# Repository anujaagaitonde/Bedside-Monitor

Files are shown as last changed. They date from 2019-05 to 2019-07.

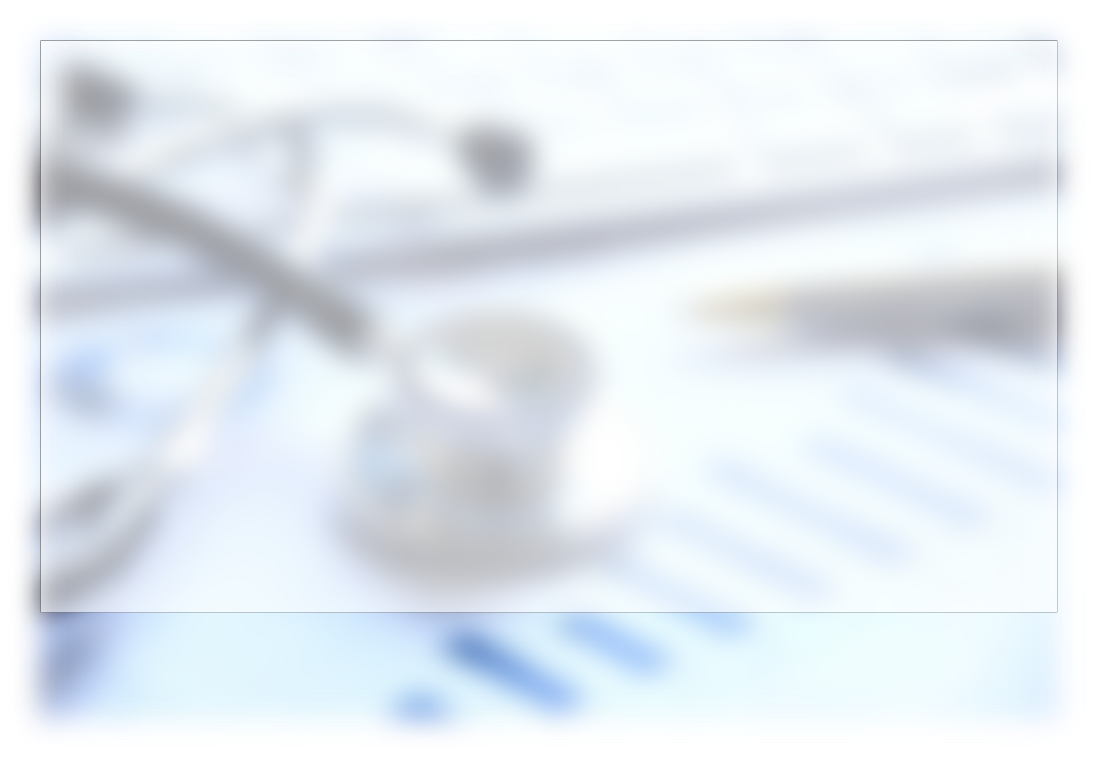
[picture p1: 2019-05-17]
Web/images/bg_image@2x.png

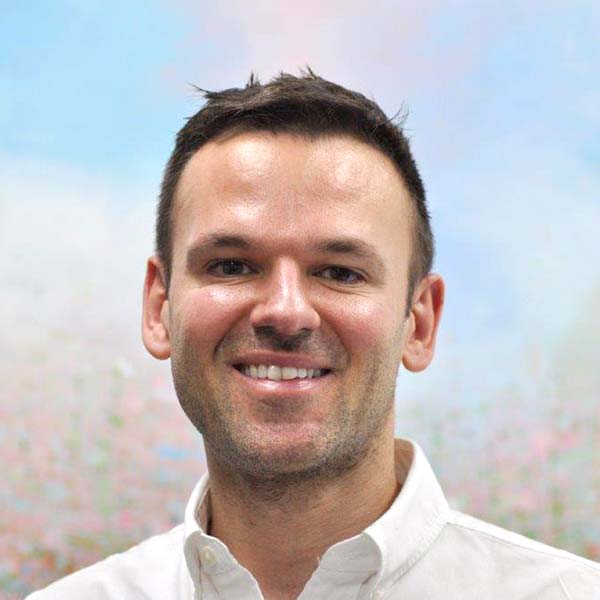
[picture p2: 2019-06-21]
Web/images/dr_profile_pic.jpg

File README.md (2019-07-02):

# LifeLine

LifeLine is a low-cost Internet-of-Things vital sign monitor with real-time illness prediction which allows doctors to monitor several patients at once from a remote location. Custom circuitry interfaces sensors to measure the patient's vital signs with any Raspberry Pi. Sensor data is displayed live on a bedside monitor and is live-streamed to a cloud-based database. A webapp allows doctors to monitor all their patients live, as well as viewing patient history over the past 24 hours. Sensor data is processed in real-time by a machine learning algorithm to detect and predict a critical event in the patient's status, which is relayed to the doctor via an instant notification in the webapp.

## Documentation

For further information about this project, visit our [wiki](https://github.com/anujaagaitonde/Bedside-Monitor/wiki):
* [1. Home](https://github.com/anujaagaitonde/Bedside-Monitor/wiki/1.-Home)
* [2. Product Design History](https://github.com/anujaagaitonde/Bedside-Monitor/wiki/2.-Product-Design-History)
* [2.1 Hardware and Firmware](https://github.com/anujaagaitonde/Bedside-Monitor/wiki/2.1-Hardware-and-Firmware)
* [2.2 Web App](https://github.com/anujaagaitonde/Bedside-Monitor/wiki/2.2-Web-App)
* [2.4 Deep Learning Model](https://github.com/anujaagaitonde/Bedside-Monitor/wiki/2.3-Deep-Learning-Model)
* [3. Meeting Records](https://github.com/anujaagaitonde/Bedside-Monitor/wiki/3.-Meeting-Records)
* [4. Innovation](https://github.com/anujaagaitonde/Bedside-Monitor/wiki/4.-Innovation)
* [5. Report of Ethical Consequences and Sustainability](https://github.com/anujaagaitonde/Bedside-Monitor/wiki/5.-Report-of-Ethical-Consequences-and-Sustainability)
* [6. Testing](https://github.com/anujaagaitonde/Bedside-Monitor/wiki/6.-Testing)
* [7. Getting Started](https://github.com/anujaagaitonde/Bedside-Monitor/wiki/7.-Getting-Started)

## About this Repository

* **[3D Printed Case:](https://github.com/anujaagaitonde/Bedside-Monitor/tree/master/3D%20Printed%20Case)** Contains 3D print and laser cut files for casing.
* **[GUI Mockups:](https://github.com/anujaagaitonde/Bedside-Monitor/tree/master/GUI%20Mockups)** Contains mockups for bedside LCD GUI.
* **[Hardware:](https://github.com/anujaagaitonde/Bedside-Monitor/tree/master/Hardware)** Contains PCB design files for PPG sensor and custom Raspberry Pi Hat.
* **[Machine Learning:](https://github.com/anujaagaitonde/Bedside-Monitor/tree/master/Machine%20Learning)** Contains illness prediction scripts.
* **[Pi:](https://github.com/anujaagaitonde/Bedside-Monitor/tree/master/Pi)** Contains the files to be run on the device Raspberry Pi and its associated libraries.
* **[Print:](https://github.com/anujaagaitonde/Bedside-Monitor/tree/master/Print)** Contains poster, leaflet and slideshow files used during demonstration.
* **[Web:](https://github.com/anujaagaitonde/Bedside-Monitor/tree/master/Web)** Contains webapp mockups and source files.

## The Project Team

* **Gasim Ahmed:** *Firmware and Machine Learning Developer*
* **Yasmin Baba:** *Hardware Designer*
* **Anuja Gaitonde:** *Web / GUI Developer and Print Promotion Designer*
* **Dayan Graham:** *Web / Cloud Developer and Casing Designer*
* **Prithvi Menon:** *Machine Learning Developer*
* **Omar Muttawa:** *Firmware Developer*

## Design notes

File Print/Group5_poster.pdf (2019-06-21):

# lifeline: THE LOW COST, IoT VITAL SIGNS MONITOR WITH REAL-TIME ILLNESS PREDICTION

## gasim ahmed, yasmin baba, anuja gaitonde, dayan graham, prithvi menon, omar muttawa academic supervisor: tim constandinou, client: miguel hernandez, mf technologies

THE PROBLEM | THE SOLUTION

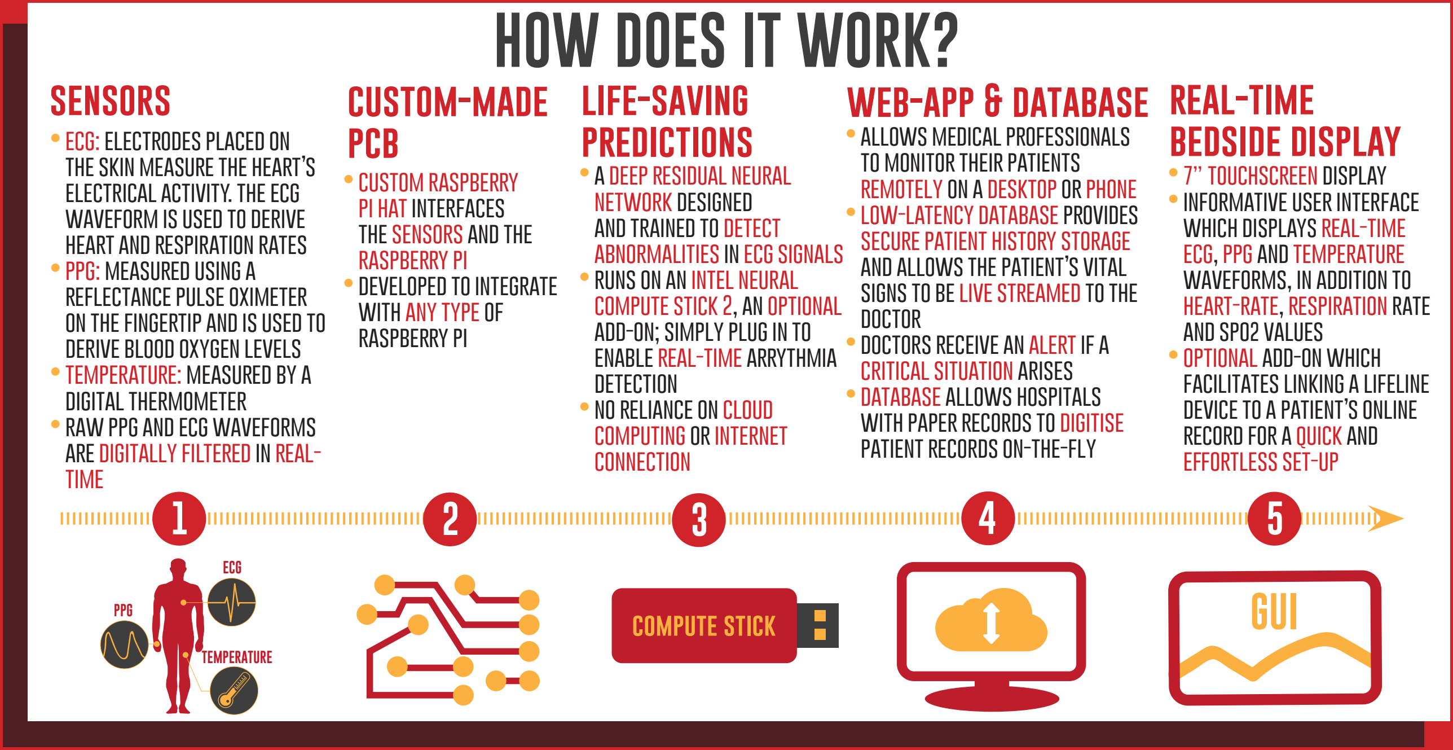
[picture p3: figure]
HOW DOES IT WORK?; sensors; custom-made; pcb; life-saving predictions; web-app & database real-time bedside display; • ecg: electrodes placed on the skin measure the heart’s electrical activity. the ecg waveform is used to derive heart and respiration rates • ppg: measured using a reflectance pulse oximeter on the fingertip and is used to derive blood oxygen levels • temperature: measured by a digital thermometer • raw ppg and ecg waveforms are digitally filtered in real- time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

# future work

## lifeline

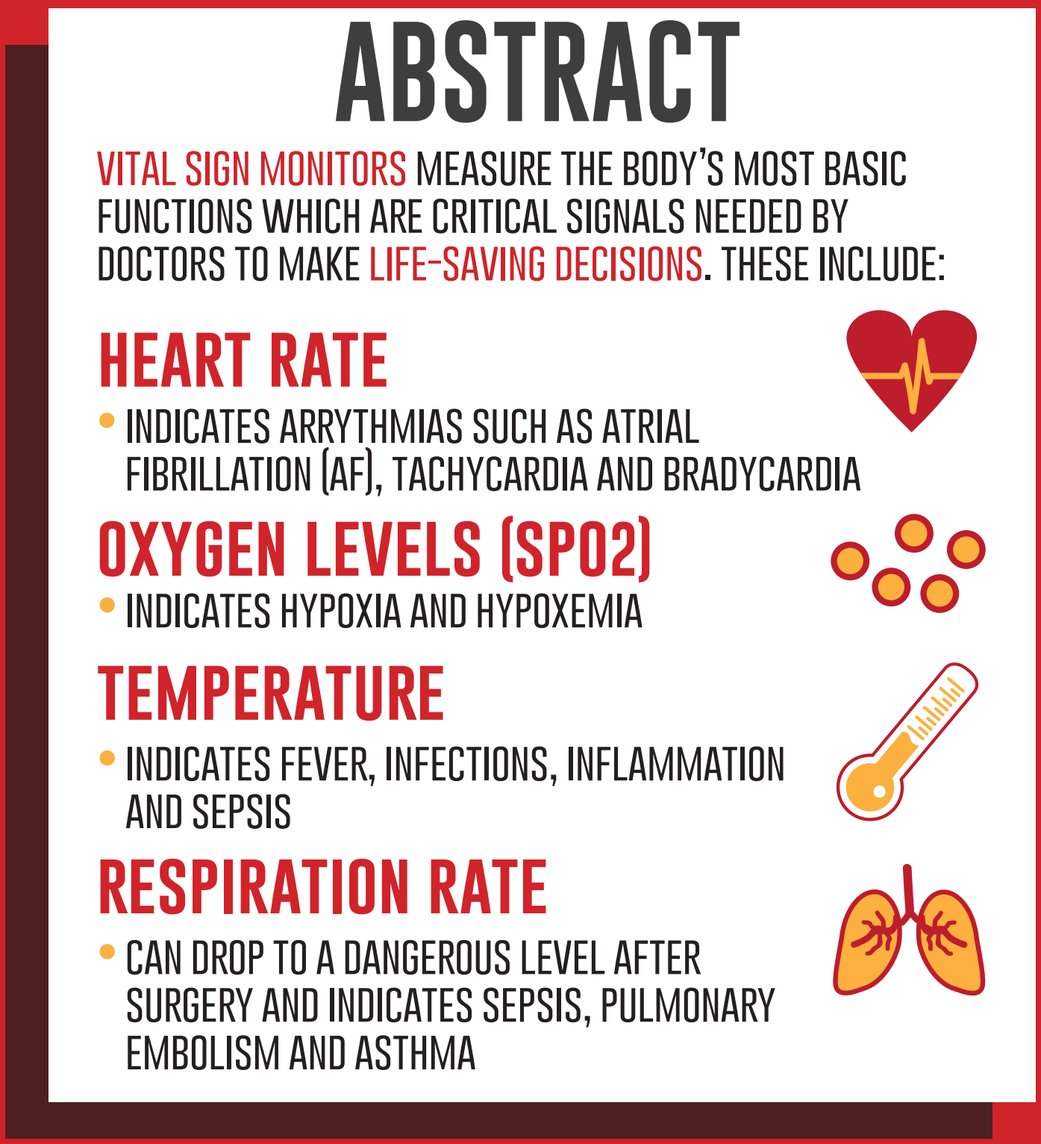
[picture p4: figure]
ABSTRACT; heart rate; oxygen levels (spo2); temperature; respiration rate; fibrillation (af), tachycardia and bradycardia; • indicates hypoxia and hypoxemia; • indicates fever, infections, inflammation and sepsis; • can drop to a dangerous level after surgery and indicates sepsis, pulmonary embolism and asthma

vital sign monitors measure the body’s most basic
functions which are critical signals needed by
doctors to make life-saving decisions. these include:

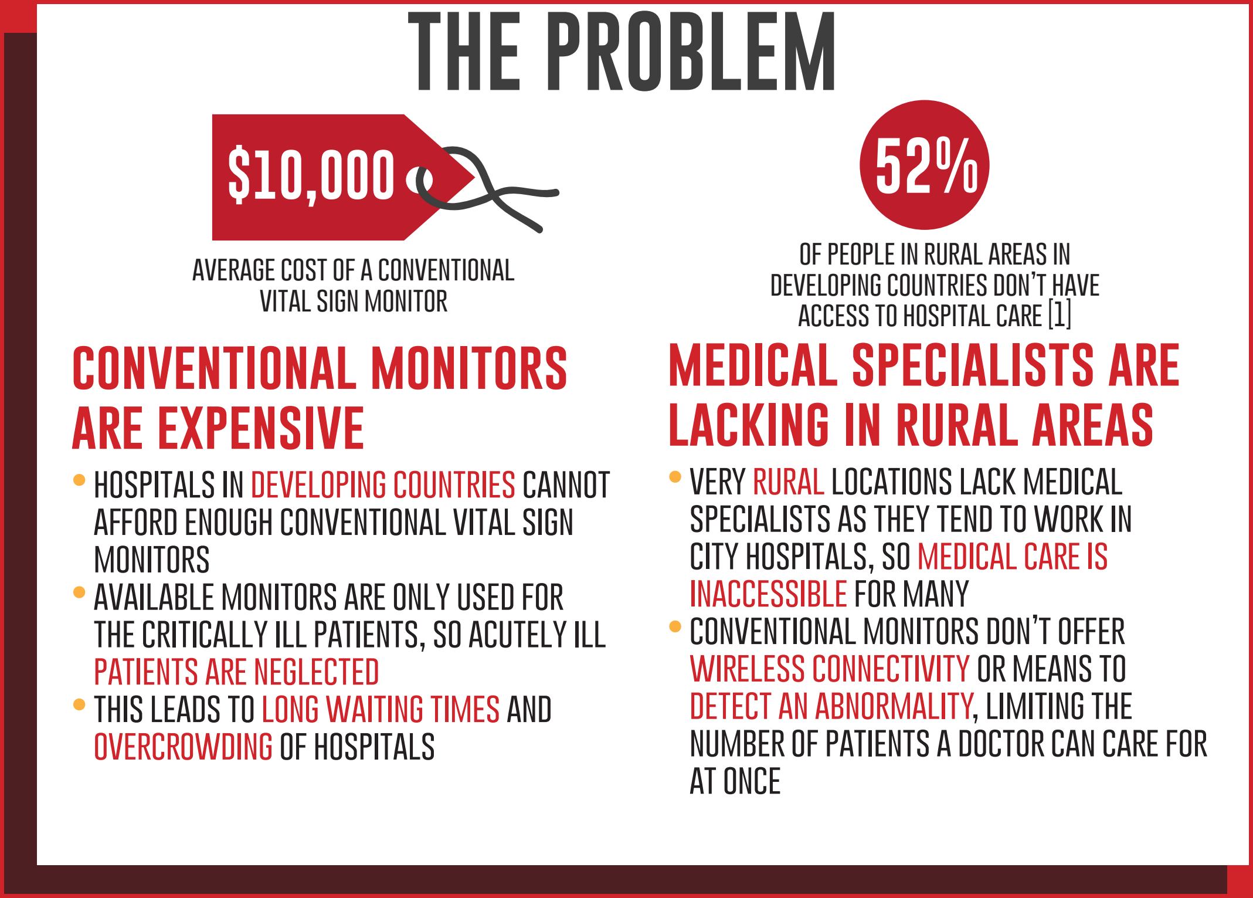
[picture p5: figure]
conventional monitors are expensive; medical specialists are lacking in rural areas; average cost of a conventional vital sign monitor; of people in rural areas in developing countries don’t have; afford enough conventional vital sign monitors • available monitors are only used for; patients are neglected • this leads to long waiting times and overcrowding of hospitals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

access to hospital care [1] • indicates arrythmias such as atrial

- hospitals in developing countries cannot

the critically ill patients, so acutely ill

- low-cost iot device that can remotely measure a patient’s vital signs from any location
- live patient data is streamed to a doctor’s desktop or phone, whilst built-in machine learning algorithms detect any abnormalities
- allows doctors to care for several patients in several locations at once, whilst alleviating the over-demand for hospital beds
- features a modular design which allows units to be customised specific to patient needs. this means hospitals can cut costs by only having to buy and / or replace the parts they actually need.
- depending on the chosen customisation option, lifeline costs between £44 -£166.
- lifeline is a durable product, housed in a secure and biodegradable 3d printed pla case

in the future, lifeline would be improved as follows:
- integrate non-invasive blood pressure monitoring
- introduce online learning to improve the abnormality detection algorithm
- research optimal digital filter methods for ecg and ppg real-time processing
- increase the accuracy and precision of the digital vital signs by
introducing more advanced signal processing techniques

number of patients a doctor can care for

[1] WORLD BANK AND WORLD HEALTH ORGANIZATION, "WHO," 13 DECEMBER 2017. [ONLINE]. AVAILABLE: HTTPS://WWW.WHO.INT/NEWS-ROOM/DE-TAIL/13-12-2017-WORLD-BANK-AND-WHO-HALF-THE-WORLD-LACKS-ACCESS-TO-ESSENTIAL-HEALTH-SERVICES-100-MILLION-STILL-PUSHED-INTO-EXTREME-POVERTY-BECAUSE-OF-HEALTH-EXPENSES.

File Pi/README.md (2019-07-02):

## Introduction
This folder contains all the firmware and software required in order to setup a lifeline monitor on a Raspberry Pi:

For setup and installation please see the [Getting-Started
](https://github.com/anujaagaitonde/Bedside-Monitor/wiki/Getting-Started) page of the Wiki:

## The following external public libraries are utilised:

### Firebase:
 - pyrebase

### PPG Processing:
 - numpy
 - scipy

### GUI:
- Matplotlib
- Tkinter

## The following libraries have been created:

### PPG Sensor and processing:
- max30102.py adapted from [Doug Burell's repo](https://github.com/doug-burrell/max30102/max30102.py)
- hrcalc.py adapted from [Doug Burrell's repo](https://github.com/doug-burrell/max30102/max30102.py)
- PPG_algorithms adapted from [Christine0313's repo
](https://github.com/Christine0313/CS244Fall2017) 

### ECG Sensor and processing:
- ECG_lib.py adapted from [PIA-Group's repo](https://github.com/PIA-Group/BioSPPy)
- ECG_processing.py

### Respiration processing:
- Resp_processing.py adapted from: [Raphaelvallat's gist](https://gist.github.com/raphaelvallat/55624e2eb93064ae57098dd96f259611)

# NOTE:
As detailed on the [
Getting Started](https://github.com/anujaagaitonde/Bedside-Monitor/wiki/Getting-Started)  page of the repo no libraries need to be manually installed, the setup script will install them automatically

<!--stackedit_data:
eyJoaXN0b3J5IjpbLTIwOTQzNTc3MTYsLTk5NDQ2MjA1NywxND
E0ODQ0NDgyLC05NjU3Mjk1MTQsMTI1ODEzMjAwNywzMDIwNzg5
LDgwODI2NDQ1NiwxNDExNTE4NDc1LDc0NDgxMjMzOF19
-->

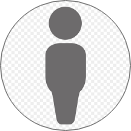
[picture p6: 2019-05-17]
Web/images/profile_pic.png

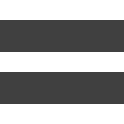
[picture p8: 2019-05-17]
Web/images/menu@2x.png

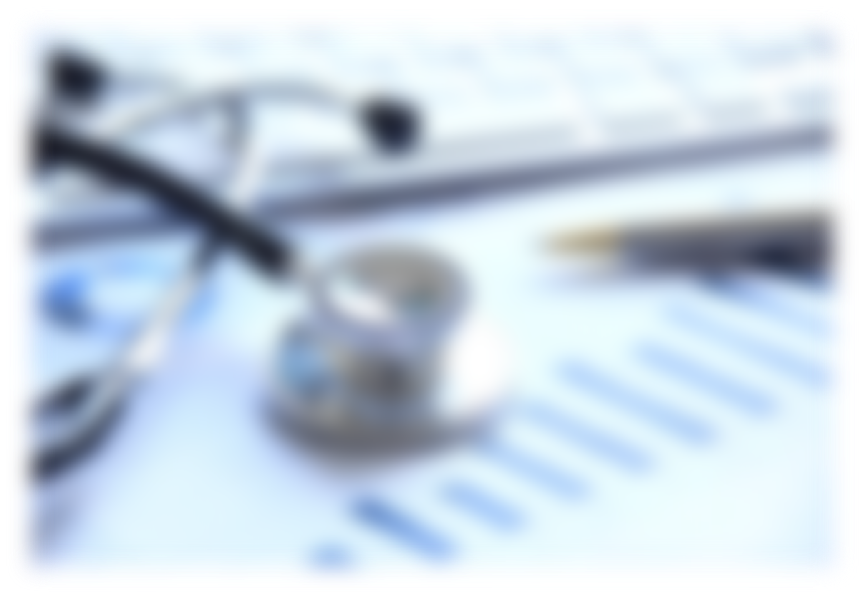
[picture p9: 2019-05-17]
Web/images/background_image.png

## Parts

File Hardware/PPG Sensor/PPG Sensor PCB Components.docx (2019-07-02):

# PCB Components - PPG

Note that all components were ordered from Imperial College London approved suppliers:

- Farnell
- RS
- Mouser Electronics
- Medisave

Cheaper options may be available from other suppliers but were not considered during this project.

# PPG Board

The following prices for the PPG Board are assuming the board is manufactured in bulk and represents the minimum cost possible. This board was not printed and built during the project.

Name on PCB | Component / Footprint | Description / Value | Supplier | Manufacturer | Unit Price(exc VAT) / £
U1 | MAX30102EFD+ | | Mouser Electronics | Maxim Integrated | 3.87
U2 | MAX14595ETA+ | | Mouser Electronics | Maxim Integrated | 1.77
U3 | MAX1921EUT18+ | | Mouser Electronics | Maxim Integrated | 1.48
R1, R2, R3, R4, R5 | 0402 SMD Resistor | 4.7 k Ω | Farnell | Multicomp | 0.0005
R6 | 0402 SMD Resistor | 4.75 k Ω | Farnell | Multicomp | 0.0004
C1, C2 | 0402 SMD Capacitor | 1 μF | Farnell | Multicomp | 0.002
C3, C4 | 0402 SMD Capacitor | 4.7 μF | Farnell | Murata | 0.0142
C5 | 0402 SMD Capacitor | 5600 pF | Farnell | Multicomp | 0.0017
C6, C7 | 0402 SMD Capacitor | 0.1 μF | Farnell | Murata | 0.0024

Total Component Cost: £7.1614

Or buy the MAXREFDES117# board ready for £19.32 (inc Handling fee and VAT) via Farnell:

https://uk.farnell.com/maxim-integrated-products/maxrefdes117/ref-des-brd-heart-rate-pulse-oximeter/dp/2627165

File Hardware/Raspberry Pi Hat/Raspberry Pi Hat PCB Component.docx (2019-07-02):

# PCB Components – Raspberry Pi Hat

Note that all components were ordered from Imperial College London approved suppliers:

- Farnell
- RS
- Mouser Electronics
- Medisave

Cheaper options may be available from other suppliers but were not considered during this project.

# Custom Raspberry Pi Hat

A price range is given for each of the following components to illustrate the cost if purchased in bulk or if purchased individually or in small packages (depends on the component). This board was printed and build during the project and the following components are the ones which were ordered and soldered on the board. They may not be the cheapest options available on the market.

Name on PCB | Component/Footprint | Description / Value | Supplier | Manufacturer | Unit Price (exc VAT) / £
U1 | LFCSP | AD8232ACPZ-WP | RS | Analog Devices | 1.82 - 4.32
U2 | MCP3008-I/SL | Analogue to Digital Converter | Farnell | Microchip | 1.31 - 1.72
R1, R2, R10, R11, R13, R14 | 0603 SMD Resistor | 10MΩ | RS | Vishay | 0.003 - 0.025
r12 | 0603 SMD Resistor | 1.4MΩ | Farnell | Multicomp | 0.0013 - 0.0019
R6, R7, R9 | 0603 SMD Resistor | 1MΩ | RS | Vishay | 0.005 - 0.03
R5 | 0603 SMD Resistor | 360kΩ | RS | TE Connectivity | 0.224 - 0.472
R3, R4 | 0603 SMD Resistor | 180kΩ | RS | Vishay | 0.004-0.024
R8 | 0603 SMD Resistor | 100kΩ | RS | TE Connectivity | 0.009 - 0.027
R15 | 0603 SMD Resistor | 10kΩ | RS | Vishay | 0.005 - 0.032
R16 | 0603 SMD Resistor | 1kΩ | RS | TE Connectivity | 0.002 - 0.032
R17, R19 | 0603 SMD Resistor | 0Ω | RS | Vishay | 0.009 - 0.018
C2 | 0603 SMD Capacitor | 1nF | RS | KEMET | 0.009 - 0.069
C1 | 0603 SMD Capacitor | 1.5nF | RS | KEMET | 0.008 - 0.043
C3 | 0603 SMD Capacitor | 10nF | RS | KEMET | 0.011 - 0.069
C5, C7 | 0603 SMD Capacitor | 100nF | RS | TDK | 0.017 - 0.069
C4, C6 | 0805 SMD Capacitor | 330nF | RS | KEMET | 0.078 - 0.206
D1 | 0603 LED | Red | Farnell | ROHM | 0.0735 - 0.206
JP2, JP6 | 3.5mm Audio Jack SMD Connector | 3 pole | RS | Switchcraft | 1.52 - 1.75
J2 | 3.5mm Audio Jack PCB Mount Connector | 4 pole | Farnell | CLIFF | 0.26 - 0.36

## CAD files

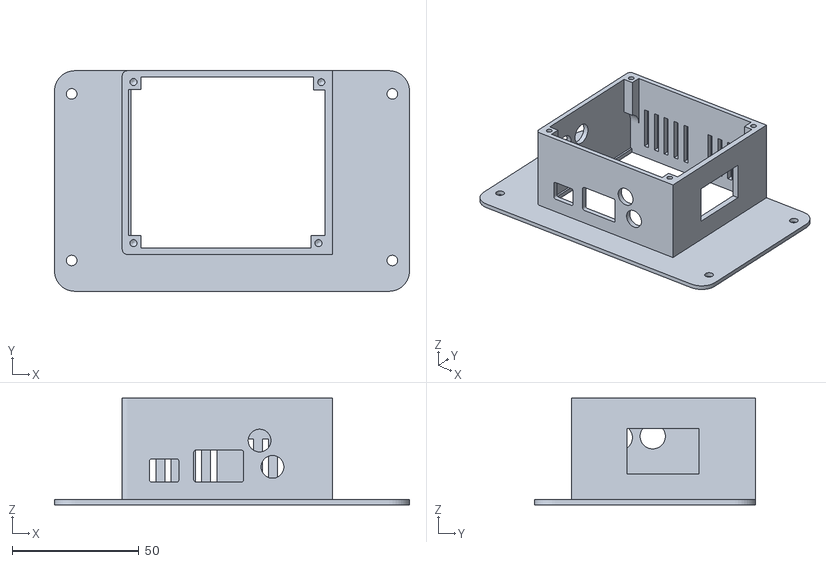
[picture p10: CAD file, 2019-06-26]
3D Printed Case/Main Case.stl
140.0 x 87.0 x 42.0

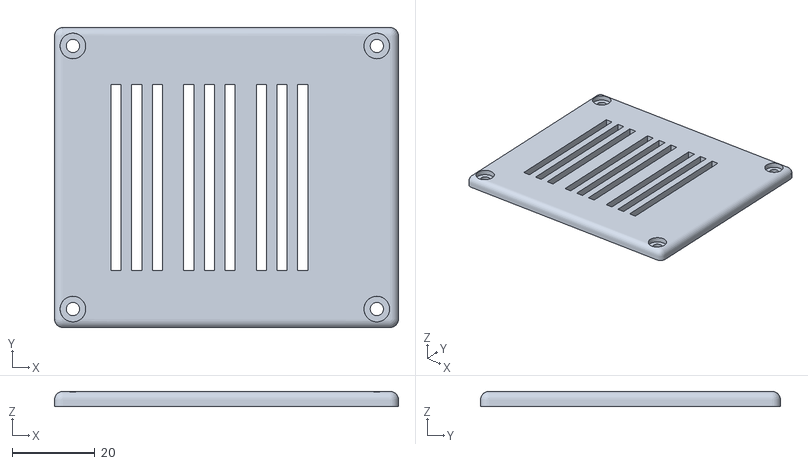
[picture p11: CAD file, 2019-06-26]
3D Printed Case/Vent Lid.stl
83.1 x 72.4 x 3.65

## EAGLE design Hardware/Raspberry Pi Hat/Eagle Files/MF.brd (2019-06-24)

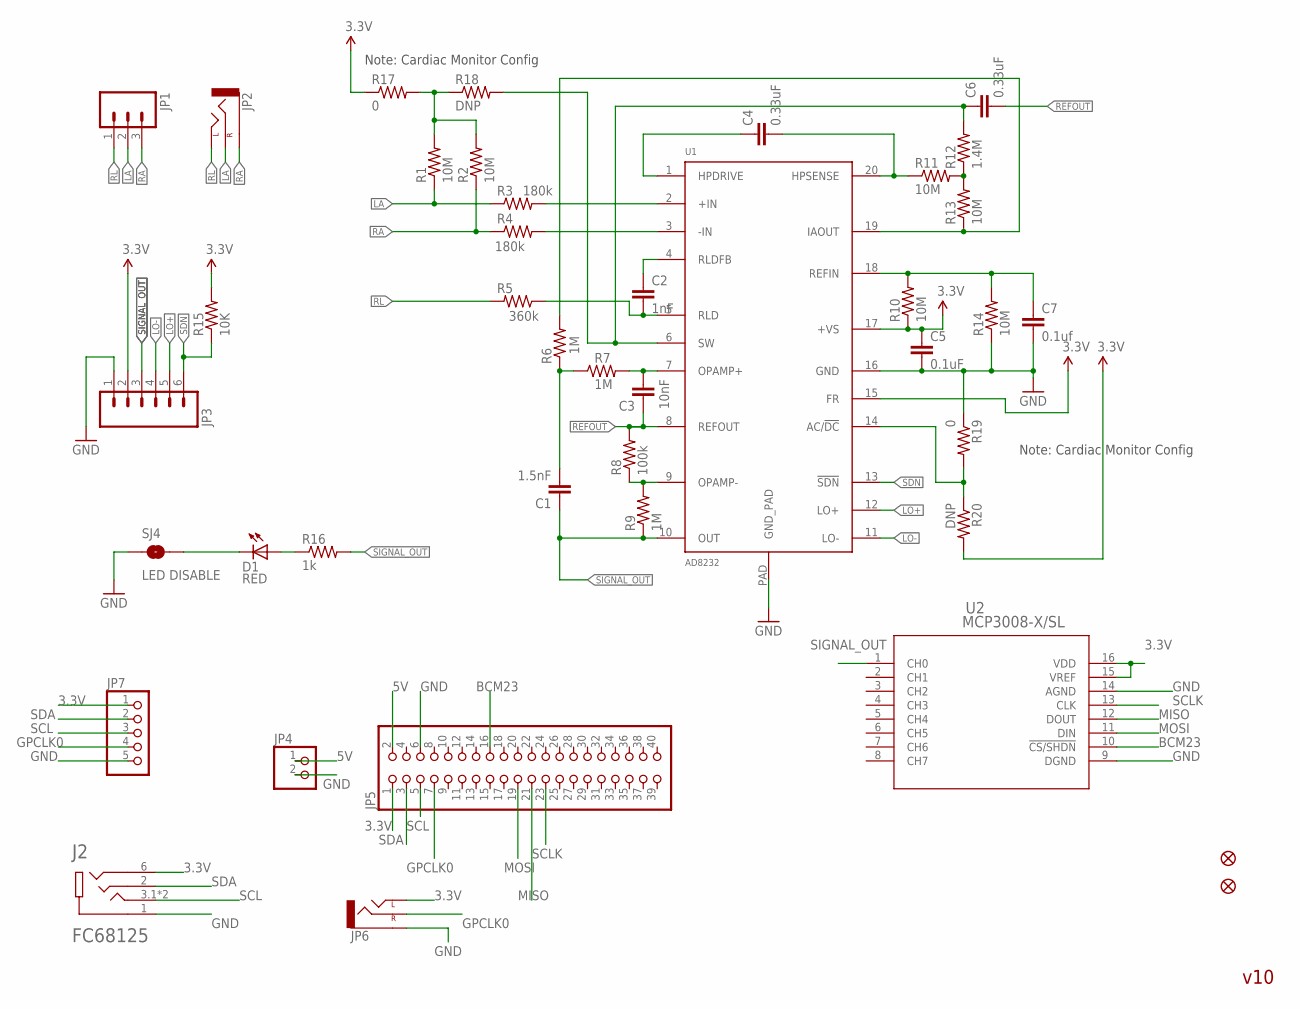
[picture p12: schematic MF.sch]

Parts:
C1: 1.5nF; 0603-CAP
C2: 1nF; 0603-CAP
C3: 10nF; 0603-CAP
C4, C6: 0.33uF; 0805
C5: 0.1uF; 0603-CAP
C7: 0.1uf; 0603-CAP
D1: RED; LED-0603
FID1, FID2: FIDUCIAL1X2; FIDUCIAL-1X2
J2: FC68125; CLIFF_FC68125
JP1: M03PTH; 1X03
JP2, JP6: AUDIO-JACKSMD2; AUDIO-JACK-3.5MM-SMD
JP3: M06SIP; 1X06
JP4: PINHD-1X2; 1X02
JP5: PINHD-2X20; 2X20
JP7: PINHD-1X5; 1X05
R1, R2, R10, R11, R13, R14: 10M; 0603-RES
R3, R4: 180k; 0603-RES
R5: 360k; 0603-RES
R6, R7, R9: 1M; 0603-RES
R8: 100k; 0603-RES
R12: 1.4M; 0603-RES
R15: 10K; 0603-RES
R16: 1k; 0603-RES
R17, R19: 0; 0603
R18, R20: DNP; 0603
SJ4: LED DISABLE; SJ_2S-TRACE
U1: AD8232; LFCSP_20
U2: MCP3008-X/SL; SOIC16-N_MC

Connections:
3.3V: C5.1, J2.6 (6SR), JP3.2, JP5.1, JP6.TIP (LEFT), JP7.1, R10.1, R15.2, R17.1, R20.2, U1.15 (FR), U1.17 (+VS), U2.15 (VREF), U2.16 (VDD)
5V: JP4.1, JP5.2
BCM23: JP5.16, U2.10 (!CS/SHDN)
GND: C5.2, C7.2, J2.1 (1S), JP3.1, JP4.2, JP5.6, JP6.SLEEVE, JP7.5, R14.1, R19.1, SJ4.1, U1.16 (GND), U1.PAD (GND_PAD), U2.9 (DGND), U2.14 (AGND)
GPCLK0: JP5.7, JP6.RING (RIGHT), JP7.4
LA: JP1.2, JP2.RING (RIGHT), R1.1, R3.1
LO+: JP3.5, U1.12 (LO+)
LO-: JP3.4, U1.11 (LO-)
MISO: JP5.21, U2.12 (DOUT)
MOSI: JP5.19, U2.11 (DIN)
unnamed: R3.2, U1.2 (+IN)
unnamed: R4.2, U1.3 (-IN)
unnamed: C3.2, R7.2, U1.7 (OPAMP+)
unnamed: C4.2, R11.1, U1.20 (HPSENSE)
unnamed: C7.1, R10.2, R14.2, U1.18 (REFIN)
unnamed: D1.A, R16.1
unnamed: R8.1, R9.2, U1.9 (OPAMP-)
unnamed: R6.2, R13.1, U1.19 (IAOUT)
unnamed: C1.2, R6.1, R7.1
unnamed: D1.C, SJ4.2
unnamed: R19.2, R20.1, U1.14 (AC/!DC)
unnamed: C4.1, U1.1 (HPDRIVE)
unnamed: R11.2, R12.1, R13.2
unnamed: C6.1, R12.2, R18.2, U1.6 (SW)
unnamed: C2.1, U1.4 (RLDFB)
unnamed: C2.2, R5.1, U1.5 (RLD)
unnamed: R1.2, R2.2, R17.2, R18.1
RA: JP1.3, JP2.SLEEVE, R2.1, R4.1
REFOUT: C3.1, C6.2, R8.2, U1.8 (REFOUT)
RL: JP1.1, JP2.TIP (LEFT), R5.2
SCL: J2.3.1 (3T), J2.3.2 (3T), JP5.5, JP7.3
SCLK: JP5.23, U2.13 (CLK)
SDA: J2.2 (2R), JP5.3, JP7.2
SDN: JP3.6, R15.1, U1.13 (!SDN)
SIGNAL_OUT: C1.1, JP3.3, R9.1, R16.2, U1.10 (OUT), U2.1 (CH0)

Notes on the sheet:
v10
Note: Cardiac Monitor Config

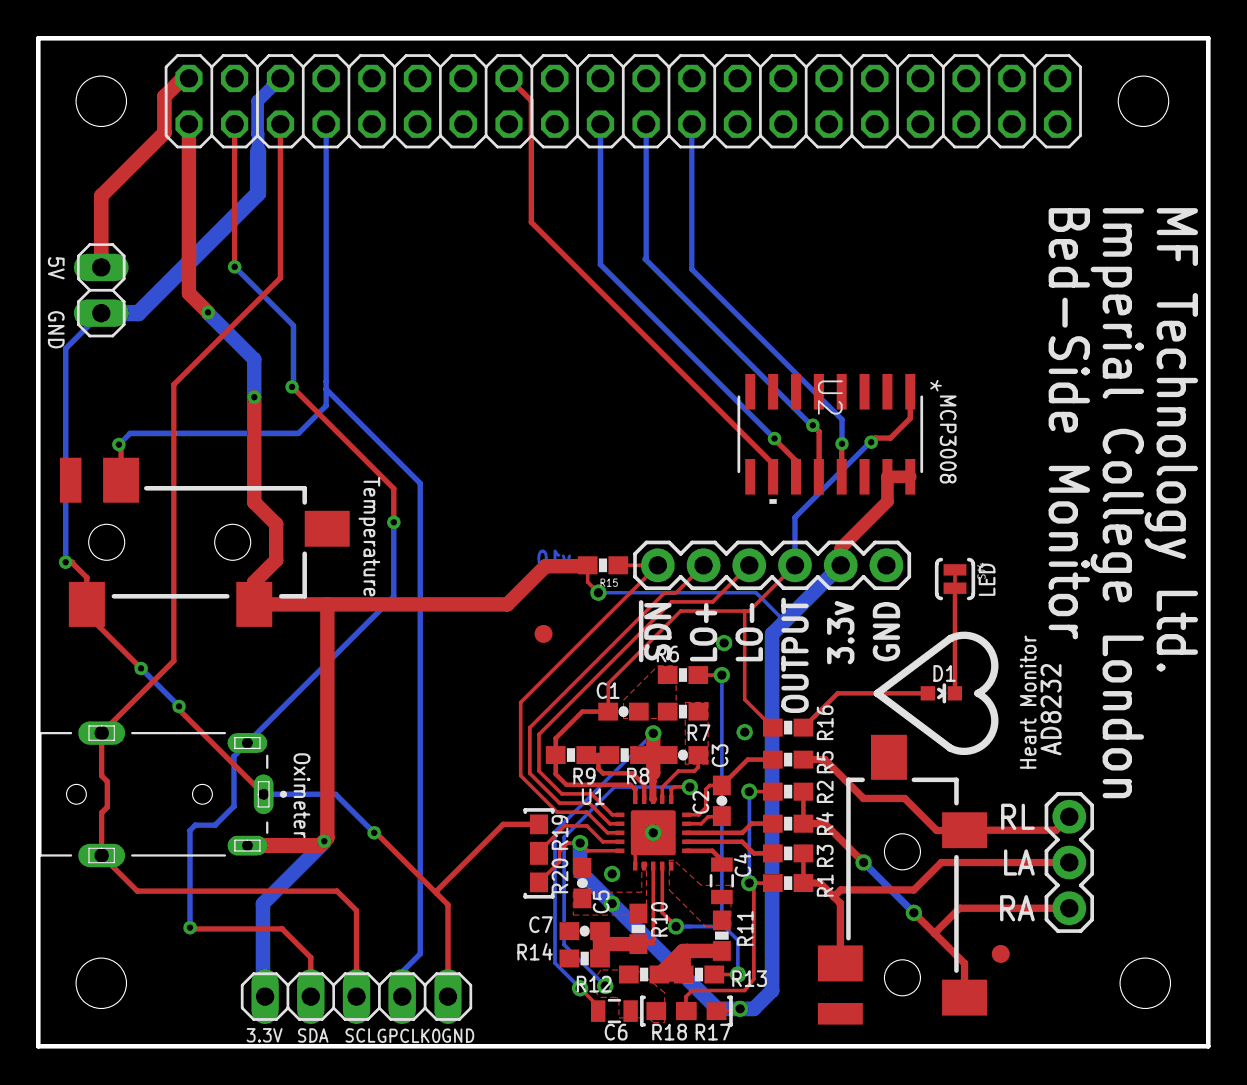
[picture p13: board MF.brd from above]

Board: 2 copper layers, 65.0 x 56.0 mm, 41 parts (0 on the bottom side), 35 nets.

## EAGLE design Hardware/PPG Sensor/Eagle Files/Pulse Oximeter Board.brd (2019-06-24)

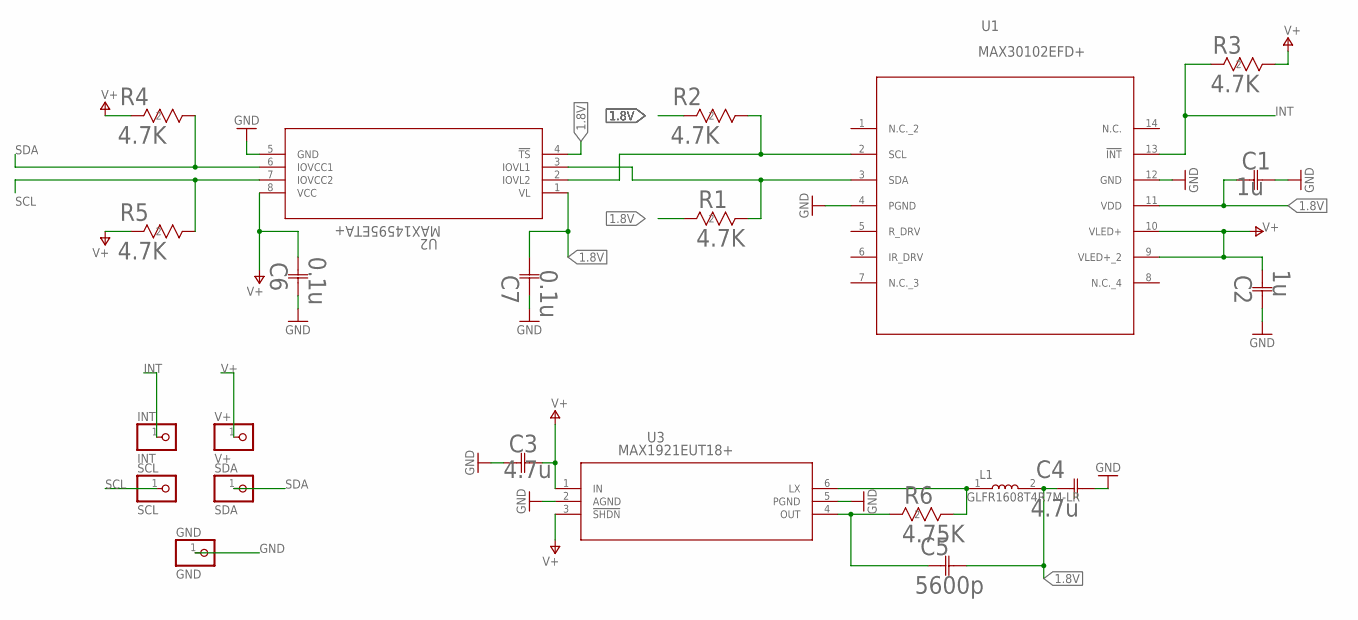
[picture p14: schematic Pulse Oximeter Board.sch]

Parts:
C1, C2: 1u; CAP_CHIP2_1X0P5
C3, C4: 4.7u; CAP_CHIP2_1X0P5
C5: 5600p; CAP_CHIP2_1X0P5
C6, C7: 0.1u; CAP_CHIP2_1X0P5
GND: GND; 1X01
INT: INT; 1X01
L1: GLFR1608T4R7M-LR; INDC1608X95N
R1, R2, R3, R4, R5: 4.7K; RES0402_CRG_TYCO
R6: 4.75K; RES0402_CRG_TYCO
SCL: SCL; 1X01
SDA: SDA; 1X01
U1: MAX30102EFD+; 21-0880B
U2: MAX14595ETA+; 21-0487A
U3: MAX1921EUT18+; 21-0058I
V+: V+; 1X01

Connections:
1.8V: C1.1, C4.1, C5.2, C7.1, L1.2, R1.2, R2.2, U1.11 (VDD), U2.1 (VL), U2.4 (!TS)
GND: C1.2, C2.2, C3.1, C4.2, C6.2, C7.2, GND.1, U1.4 (PGND), U1.12 (GND), U2.5 (GND), U3.2 (AGND), U3.5 (PGND)
INT: INT.1, R3.2, U1.13 (!INT)
unnamed: R2.1, U1.2 (SCL), U2.2 (IOVL2)
unnamed: L1.1, R6.1, U3.6 (LX)
unnamed: R1.1, U1.3 (SDA), U2.3 (IOVL1)
unnamed: C5.1, R6.2, U3.4 (OUT)
SCL: R5.1, SCL.1, U2.7 (IOVCC2)
SDA: R4.1, SDA.1, U2.6 (IOVCC1)
V+: C2.1, C3.2, C6.1, R3.1, R4.2, R5.2, U1.9 (VLED+_2), U1.10 (VLED+), U2.8 (VCC), U3.1 (IN), U3.3 (!SHDN), V+.1

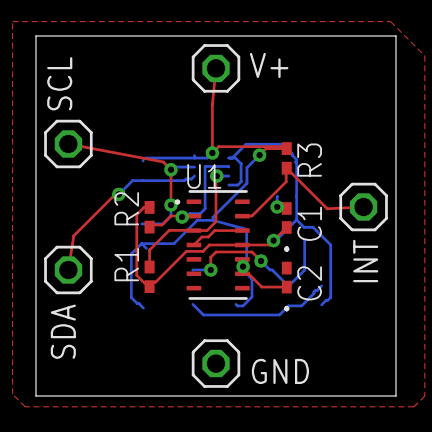
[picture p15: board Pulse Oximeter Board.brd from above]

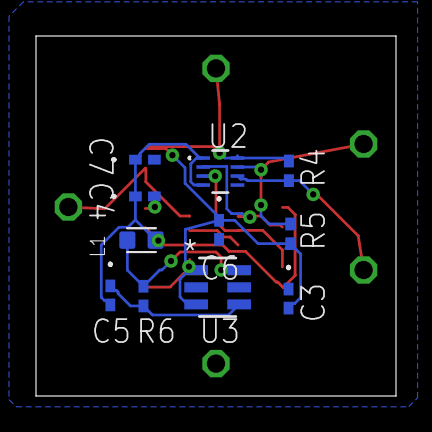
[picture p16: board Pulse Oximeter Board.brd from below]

Board: 2 copper layers, 20.0 x 20.0 mm, 22 parts (11 on the bottom side), 10 nets.

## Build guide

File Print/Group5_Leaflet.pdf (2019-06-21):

### Group 5 - Bedside Monitoring: - Gasim Ahmed - Yasmin Baba - Anuja Gaitonde - Dayan Graham - Prithvi Menon - Omar Muttawa

### To be printed on A3 paper, cut out and folded into a heart shape, as

seen in hard copy submitted to the teaching office.

# lifeline

THE LOW-COST,

# IoT VITAL SIGNS MONITOR

# cost

# market size

# composition and recycling

- modular design allows broken or misplaced parts to be replaced without having to replace the whole device.
- our initial target market is developing countries around the world, where basic healthcare is less accessible.
- lifeline’s pcb and all circuitry is housed in a 3d-printed pla casing, which is biodegradable.
- if the device or any of its components is no longer needed, send it back to us
and we will recycle or
correctly dispose of it
for free!
- in 2018, the market size for remote vital sign monitors was valued at $684 million and is expected to rise to $1,727 million by 2026³

- lifeline is the cheapest of its kind on the market
to date, costing between
£44-£166 to mass produce,
depending on chosen
customisation options.

2018 2026

1 Source: World Bank and WHO: https://bit.ly/2KIJIwc 2 Source: World Health Organisation: https://bit.ly/2XtGtdW 3 Source: Acumen Research and Consulting: https://bit.ly/2KzOVEL

# lifeline

THE LOW-COST,

# IoT VITAL SIGNS MONITOR

# THE NEED FOR A REMOTE PATIENT MONITOR

# WHAT MAKES US DIFFERENT?

# HOW DOES IT WORK?

vital sign monitors measure the body’s temperature, oxygen, and heart and respiration functions which are critical signals doctors need to make life saving decisions.

- ecg: used to derive heart rate
- ppg: used to derive spo2 and respiration rate
- temperature: indication of
infection and inflammation
- custom made pcb interfaces sensors with any
raspberry pi which sends raw sensor data to the
hospital’s database using the internet
- runs machine learning algorithms to detect and predict atrial fibrillation and other abnormalities
- stores real-time patient data and patient history
- allows doctor to remotely monitor their patients in real-time and receive alerts about abnormalities
- allows monitoring at the bedside for carers

unlike other existing remote monitors, lifeline features:
modular design allowing units to be built custom to patient needs and / or budget. accurate sensors allowing for medical certification and is compliant with data safeguarding regulations.
machine learning algorithms to detect, predict and alert doctors of abnormalities in a patient’s vital signs.
intuitive user interface for hospitals to monitor several patients live at once.

lifeline is a low-cost, IoT device which remotely streams vital sign measurements to a nearby hospital, allowing doctors to look after many patients in many locations at once.

average cost of a conventional vital sign monitor

of people in developing countries
don’t have access to hospital care¹

percentage of people in
developing countries admitted to hospital due to overcrowding²

## sensors

## custom raspberry pi hat

## raspberry pi screen (optional)

## intel neural compute stick 2 (optional)

## low-latency cloud database

## webapp

TEMPERATURE

ECG

PPG | 1

2

3

4

5

6

conventional vital sign monitors are unaffordable for rural hospitals in developing countries leading to long waiting times, overcrowding of hospitals and neglection of less critical patients.

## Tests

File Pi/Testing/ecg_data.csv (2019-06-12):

9.120000000000044338e+02
9.120049193447924836e+02
9.119441218390314816e+02
9.112492070271886178e+02
9.083119890503373881e+02
9.010437297616625756e+02
8.891325356702333238e+02
8.760309165591289684e+02
8.677264474141554729e+02
8.682412392043822820e+02
8.757963039609683165e+02
8.838022096616863337e+02
8.863082486314107200e+02
8.829102513310797349e+02
8.784152627675829308e+02
8.776778147310678833e+02
8.808775328174579045e+02
8.839549633740303989e+02
8.834129324757010409e+02
8.801867656227900625e+02
8.784909148540464230e+02
8.810126875082322613e+02
8.857747360140754154e+02
8.881570335404998104e+02
8.858928451236658930e+02
8.815786719285578101e+02
8.799451111581386158e+02
8.828512127377488241e+02
8.874125533943711162e+02
8.892094270356074048e+02
8.870475466066282024e+02
8.841281997942929820e+02
8.843682482259270046e+02
8.879315113901300265e+02
8.909843611101294982e+02
8.900419710303128795e+02
8.861841219728643182e+02
8.844708800005222429e+02
8.889525894898569049e+02
8.984400978502601447e+02
9.075482184793606848e+02
9.119397520062050262e+02
9.122272207064249869e+02
9.125018448186157229e+02
9.152216159737595262e+02
9.180392191808286952e+02
9.160495628592932462e+02
9.071573857713202642e+02
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

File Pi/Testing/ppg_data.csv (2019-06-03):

2.934700000000000000e+04
2.934700000000000000e+04
2.935600000000000000e+04
2.936600000000000000e+04
2.936200000000000000e+04
2.936700000000000000e+04
2.937500000000000000e+04
2.937800000000000000e+04
2.937700000000000000e+04
2.938000000000000000e+04
2.939200000000000000e+04
2.938800000000000000e+04
2.939600000000000000e+04
2.940400000000000000e+04
2.941400000000000000e+04
2.941300000000000000e+04
2.943300000000000000e+04
2.943500000000000000e+04
2.944300000000000000e+04
2.945100000000000000e+04
2.945900000000000000e+04
2.947500000000000000e+04
2.948700000000000000e+04
2.948700000000000000e+04
2.949600000000000000e+04
2.950100000000000000e+04
2.951200000000000000e+04
2.951800000000000000e+04
2.953300000000000000e+04
2.953500000000000000e+04
2.954000000000000000e+04
2.954500000000000000e+04
2.954400000000000000e+04
2.955000000000000000e+04
2.955100000000000000e+04
2.955500000000000000e+04
2.955700000000000000e+04
2.955800000000000000e+04
2.957500000000000000e+04
2.957700000000000000e+04
2.957600000000000000e+04
2.958200000000000000e+04
2.958000000000000000e+04
2.957900000000000000e+04
2.958700000000000000e+04
2.958900000000000000e+04
2.960000000000000000e+04
2.960900000000000000e+04
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

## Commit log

2019-05-17 Update patient dashboard
2019-05-17 make patient dashboard redirect to live view
2019-05-21 add starred functionality to database, filter screens by starred and critical
2019-05-30 format patient view and add url, also add new patient screen
2019-05-31 Added 20 second sample data of PPG signal
    [ppg_data.csv]
2019-05-31 make patient dashboard tabbed and add a loader
2019-06-03 first stage of implementation of gui
    [ppg_data.csv]
2019-06-07 working version of gui + data for experiment
    [ecg_data.csv, ppgir_data.csv, ppgred_data.csv]
2019-06-12 First working version
    [ecg_data.csv]
2019-06-12 new ecg data
    [ecg_data.csv]
2019-06-20 First stage of picode clean-up
    [ecg_data.csv, ppg_data.csv, ppgir_data.csv, ppgred_data.csv]
2019-06-21 added web mockups and print media
2019-06-24 Added hardware files
    [MF.brd, MF.sch, Pulse Oximeter Board.brd, Pulse Oximeter Board.sch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]
2019-06-24 added print statements to setup.py
2019-06-26 add 3d printed files
    [Main Case.stl, Vent Lid.stl]
2019-06-27 rearrange repo
    [Main Case.stl, Vent Lid.stl]
2019-06-27 rename folders
    [ecg_data.csv, ppg_data.csv, ppgir_data.csv, ppgred_data.csv]
2019-07-04 First Complete PyQtTest.py
    [resp_data.csv]

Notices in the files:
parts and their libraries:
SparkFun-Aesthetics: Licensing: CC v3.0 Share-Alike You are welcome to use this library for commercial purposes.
